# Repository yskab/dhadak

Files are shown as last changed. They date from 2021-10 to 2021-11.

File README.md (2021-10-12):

# धड़क\Dhadak - A Pulse Oximeter

<p align="middle">
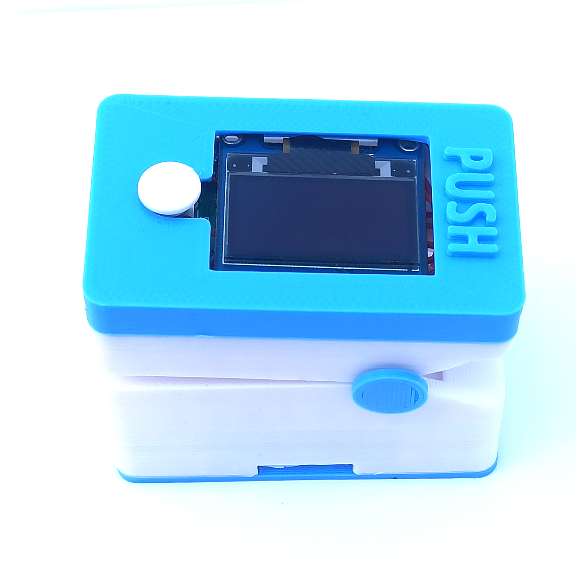
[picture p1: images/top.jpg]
  
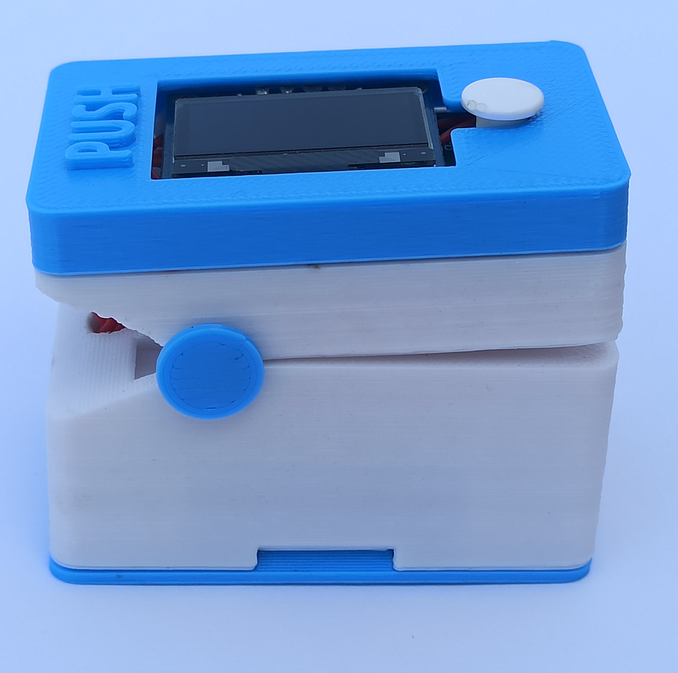
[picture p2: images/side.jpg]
   
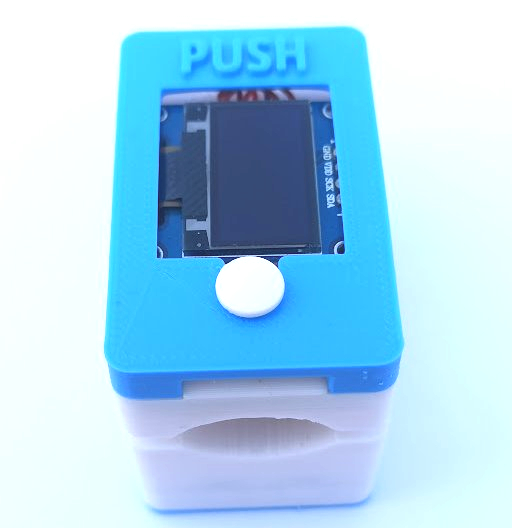
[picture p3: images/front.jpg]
  
</p>

* [Overview](#Overview)
* [Specifications](#Specifications)
* [Documentation](#Documentation)
* [Usage](#Usage)
* [Credits](#Credits)

## Overview

धड़क is a Pulse Oximeter which plugs onto a finger and measures
SpO<sub>2</sub>% and Heart rate of person.

<p align="center">
  spo2_gif
</p>

* Design doesn't use any specific oximeter sensor. A photodiode is used in the front end along with clean and amplify stages to obtain a suitable signal.

* ATmega4808 microcontroller is used in design along with QSB34CGR photodiode.

***Project Youtube video***

<div align="center">
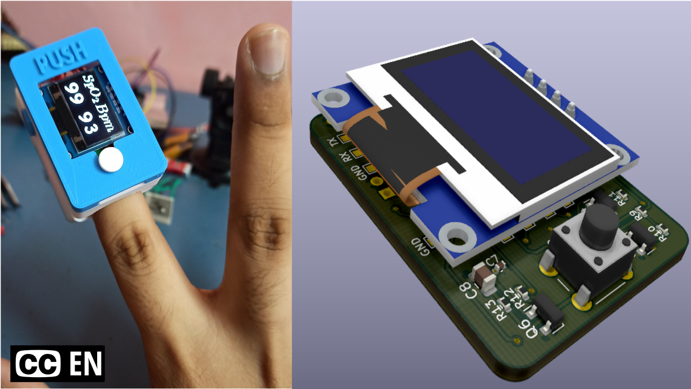
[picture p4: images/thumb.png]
Project Youtube video:
  
</div>

It was quite difficult to build a device that would work accurately for all finger types. Still, there are issues/improvements which I could think of in design, code & enclosure. Hence I decided to create an improvements section in each specific readme for the project directory. Anyone interested in building this project can refer to it and create a better device.

## Specifications
* Runs on 2 AAA Batteries (MN2400).
* Takes 15 secs max to find parameters (can find earlier, depends on subject's skin as leds adjust intensity to obtain a good response).
* Max average current draw: 25mA( This is the maximum draw when leds at full brightness). As per battery's datasheet and minimum operating voltage of 2.7V, this would give a continuous operation time of 13hrs. 
* 3 sec display update rate.
* Battery percentage indicator.
* Snap-fit enclosure with spring mechanism which ensures good firm contact of finger with photodiode.
* Soft latch power On/Off main button.
* 17KB Flash memory usage.

## Documentation

Complete understanding document detailing the overview, circuit design, block diagrams, and algorithm is available below for 2 languages:

[हिंदी दस्तावेज़](https://github.com/yskab/dhadak/blob/main/doc/hi/dhadak_hi.pdf)

[English doc](https://github.com/yskab/dhadak/blob/main/doc/en/dhadak_en.pdf)

## Usage
Repository Structure:

* **dhadak:** KiCAD Project files for v1.
* **dhadak_v2:** KiCAD Project files for v2.
* **doc:** Contains source for documentation.
* **enclosure:** FreeCAD project file.
* **firmware:** Source code.
* **images:** Device Images.
* **references:** PDF documents which were used as a reference to create the project.

Device was built as per KiCAD project: /dhadak. During testing, I later discovered that some things were simply not required to be added in design, so I desoldered certain circuit sections, amended the design, and wrote updated code/documentation around it. 

If you wish to build this device, please refer /dhadak_v2 project, it has the updated final schematics as per amendments in v1. Though PCB design was not done for this updated version, you can use the schematics present in the directory and build a PCB for it. Changes/amendments from v1 are mention in /dhadak_v2/readme.

### Programming Device

* For ATmega4808 first burn fuse to change clock to internal 8MHz.

* Proceed with code upload.

* Insert finger and press power button, wait for values to appear.

Please ensure to use good leds recommended for oximetry. I worked with generic ir & red leds which are used for indication applications hence SpO<sub>2</sub> was not quite accurate (as a healthy individual I should have got readings around 97+ but used to get around 90. This is the reason a small scaling factor has been added in code to compensate and calculate higher reading). These indication LEDs should not be used for oximeter. For best response, ensure LEDs have:

* Narrow view angle for less dispersion and deeper penetration into the skin.
* Rectangular package in the clear lens so that finger can rest comfortably.
* High radiant power.
	
A suitable choice can be Vishay Semiconductor's VSMD66694 or any other equivalent.

## Credits

**OLED Library:** ssd1306 by lexus2k

https://github.com/lexus2k/ssd1306

**OLED Images:** bmp2hex by Robert Gallup

https://github.com/robertgallup/python-bmp2hex

**Heart rate Algorithm:**

ArgÃijello-Prada, Erick Javier. The mountaineer’s method for
peak detection in photoplethysmographic signals. Revista Facul-
tad De Ingenieria-universidad De Antioquia 2018 (2019): 42-50

https://api.semanticscholar.org/CorpusID:116767900

**SpO<sub>2</sub> Algorithm:**

Michael W. Wukitsch, BA,Michael T. Petterson, BA, RRT, CPFT,
David R. Tobler, BSEE,and Jonas A. Pologe, BSEE
PULSE OXIMETRY: ANALYSIS OF THEORY, TECHNOLOGY, AND PRACTICE

https://link.springer.com/article/10.1007%2FBF01617328

All application notes/papers consulted in design can be found in the references directory.

## License
MIT License

Copyright (c) 2021 Y S K Abhijeet

Permission is hereby granted, free of charge, to any person obtaining a copy
of this software and associated documentation files (the "Software"), to deal
in the Software without restriction, including without limitation the rights
to use, copy, modify, merge, publish, distribute, sublicense, and/or sell
copies of the Software, and to permit persons to whom the Software is
furnished to do so, subject to the following conditions:

The above copyright notice and this permission notice shall be included in all
copies or substantial portions of the Software.

THE SOFTWARE IS PROVIDED "AS IS", WITHOUT WARRANTY OF ANY KIND, EXPRESS OR
IMPLIED, INCLUDING BUT NOT LIMITED TO THE WARRANTIES OF MERCHANTABILITY,
FITNESS FOR A PARTICULAR PURPOSE AND NONINFRINGEMENT. IN NO EVENT SHALL THE
AUTHORS OR COPYRIGHT HOLDERS BE LIABLE FOR ANY CLAIM, DAMAGES OR OTHER
LIABILITY, WHETHER IN AN ACTION OF CONTRACT, TORT OR OTHERWISE, ARISING FROM,
OUT OF OR IN CONNECTION WITH THE SOFTWARE OR THE USE OR OTHER DEALINGS IN THE
SOFTWARE.

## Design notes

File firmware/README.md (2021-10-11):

***src/main.cpp*** - source code

***src/bitmap.h*** - bitmap array of displayed images

***lib/ssd1306*** - ssd1306 library - https://github.com/lexus2k/ssd1306

Upload and device options configured in platformio.ini

Memory Usage:

RAM: 7.2% (used 441 bytes from 6144 bytes)

Flash: 35.3% (used 17327 bytes from 49152 bytes)

## Suggested Improvements

* Design can be comfortably completed on a 32KB flash device including any additional improvements. I had 10 units of ATmega4808, hence used it.

* Microseconds Delay in main loop sets the per-sample frequency (red and ir signal frequency) at around 500Hz. This is not a suitable approach, a better approach is to use timers, but I decided not to as it just worked fine.

* There is a slight step in the DAC Diff square wave signal before and after the sample signal. This is happening because DAC is called twice in a short interval( first to set diff level and then to set led brightness). This causes DACs diff output to add that slight step, though it's outside the signal, still a better approach is to improve the design and remove the step completely.

<p align="middle">
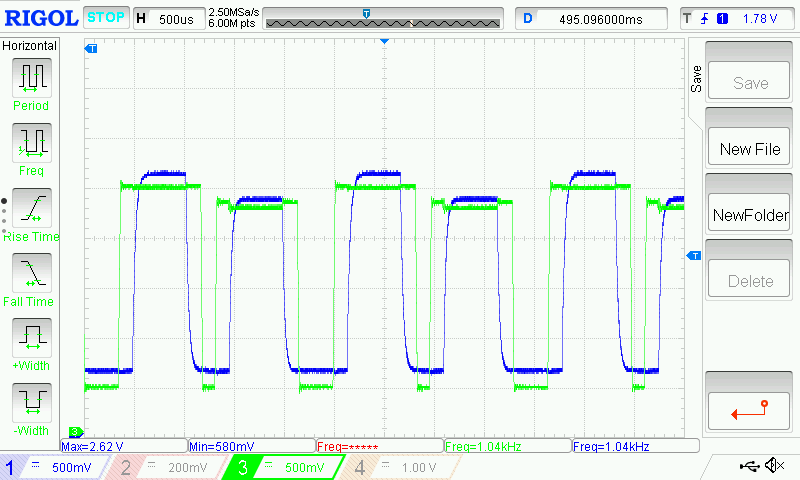
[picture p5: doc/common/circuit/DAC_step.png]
  
</p>

* Additional Algorithm can be implemented to take care of any motion-related errors.

* Generated diff signal can be made adaptable with I to V signal so that any slight variation in finger pressure or signal wobble, a new diff signal is immediately calculated and subtracted.

* Oled Updates values in real-time.

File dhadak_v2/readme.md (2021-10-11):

This KiCAD directory has the updated v2 schematics. PCB was not designed, PCB in v1 was amended to this schematic, so the actual code and documentation refer to this design. Changes in this schematics, when compared with v1, are:

* Increased Transimpedance Stage resistance to 576K. 200K was a bit lower, it is important to get a good response at this stage, hence the resistor was doubled.

* All resistors in difference amplifier changed to 10K. There is no need to have gain here. Fixed ADC ref at 1.1V and with oversampling, the response is quite good. Amplification can be added later in PGA.

* Removed isolation stage completely. No requirement to have separate isolation and Gain stages.

* A Single PGA stage is added, so any gain is applied equally to both red and ir.

* For a Quad opamp package, 1 opamp was left, so used it as a buffer.

* Removed R7 in series with infrared led. No need to limit ir current.

* 10u Bypass Cap on DAC didn't make any difference in ringing, removed it.

* Improved the Soft-latch circuit. Earlier Latch output was being used directly as Vcc. Since there are individual bypass capacitors also connected to DAC, ATmega, opamp, On to Off state was not working as the bypass capacitors were charged keeping the latch always turned On. In amended design, latch is completely local and Mosfet output drives Vcc, so latch can turn Off comfortably.

## Suggested Improvements
* A better PCB layout for I2C signals.
* Better bypassing of DAC, there was slight ringing at the edges, hence had to use a small delay before and after the waveform so that no spikes get included in difference amplifier output edges.

<p align="middle">
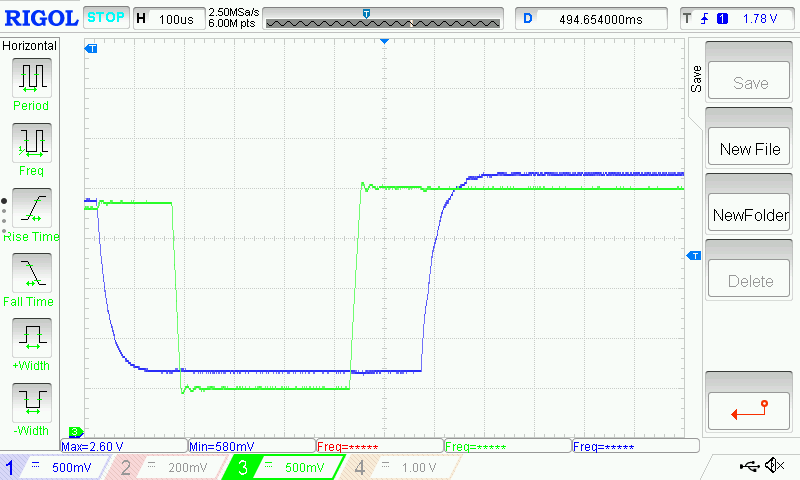
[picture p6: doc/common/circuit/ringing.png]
  
</p>

* Enclosure size was made as per battery lengths, PCB dimension could have been increased, allowing all the parts to fit in back, this would allow easy reflow of the backside and no hand soldering.

## Credits

* Latch circuit is taken from user Sam Raja's comment under EEVblog's Video: [EEVblog #262 - World's Simplest Soft Latching Power Switch Circuit](https://youtu.be/Foc9R0dC2iI)

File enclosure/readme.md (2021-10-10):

STLs folder has the actual STL files which i used for printing. I don't own a printer, so i sent the files to a external printing service who printed and shipped to me. Models were printed in PLA with 20% infill and with supports.

Minimum Finger Height: 9mm, if more than this, spring action takes place
Maximum Finger Width: 20mm	

## Suggested Improvements
* top part's snap fit is is a bit tight, it's hard to fit and remove, need to add some clearance.
*  Battery holding rectangle structures are asymmetrical, not equal dimensions.
* Some Spring inserts were tight but was able to fit at least one, which is good enough for test purposes and keeps pressure on the finger. A better design can be used for spring inserts instead of cylindrical holes. Also, actual springs can be used instead of re-purposing safety pins.

*   The pivot(circular tab part) was not able to fit in the spring  hinge as it was difficult to line up the spring with holes. Should have measure the lengths of springs before cutting them.

*   PCB fits nice, also when the top is closed, there is no wobble and things are tight.
*   It can be a bit difficult to put springs inside, doable with tweezers.
*   The battery wiring hole was a bad idea. It is difficult to get the wire through battery clips and supports had to be removed from that area which is difficult to do. Internal supports took a lot of time to remove so battery (+),(-) wiring needs a better approach.
*   upper wall in the led compartment should have been a little lower to allow the led to sit properly instead of slipping into the led wiring hole.
*   Led compartment should have been tighter to avoid glue.
*   I ordered wrong kind of battery clips. These were intended for series connections not for holding 2 AAAs. Had to snap one in half so that I can get (+) and (-).
*   Design to avoid internal support structures as they are difficult to remove.

## Credits for used external models

* Led: https://grabcad.com/library/3mm-led

* Switch 6x6: https://grabcad.com/library/tactile-switch-thru-6mm-series-1

* AAA Battery: https://grabcad.com/library/aaa-batterie-1

* Battery contact clip: https://www.keyelco.com/product.cfm/Slide-In-AAA-Battery-Contacts/5213/product_id/893

* Photodiode: https://octopart.com/qsb34cgr-on+semiconductor-84331133#CadModels

## Credits for Tutorials
As a complete beginner in FreeCAD, listed tutorials below helped me a lot to get to speed and start working on my model. I referred them throught the design. I would suggest anyone who is a beginner to start with these tutorials below for FreeCAD:

[Forum Discussion - Electronic Enclosure Arduino](https://youtu.be/6Nu8y0C0nvg)
Channel: [Learn FreeCAD](https://www.youtube.com/channel/UC_9HwDkwxllq5lFGkYBIH9g)

[FreeCad 0.18 Training Video inc. Kisslicer 3D Slicer](https://youtu.be/3w466yb255A)
Channel: [Ha Gei](https://www.youtube.com/channel/UCoe3BcVuLC9I2_yFud5vp8Q)

[FreeCAD Electronic Enclosure Using Simple Parametric Design Techniques](https://youtu.be/cJfbINgyz-k)
Channel: [Adventures in creation](https://www.youtube.com/channel/UC7pokUsRb6q2B0FOzSqQLlw)

Great tutorial by Adafruit for making snap fit cases
[# Layer by Layer – PyBadge Snapfit Case Pt 3](
https://youtu.be/pfBXfgCTmAU)

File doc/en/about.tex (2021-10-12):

During the COVID-19 wave in India, I saw a lot of people buying oximeters from medical stores and online to monitor oxygen levels at home. I was quite intrigued, how can a small device plugged to a finger could calculate heart rate and oxygen saturation? This question got me started to research and understand how these things actually work and whether I can make one from scratch. In the process I realized, it would be helpful to write all details in an understanding document which will serve as a memory to me and can be of help to others too.
Also, I wanted to start learning \LaTeX \hspace{1pt} so as to create beautiful written documents for all future projects.\medskip

This writing tries to present a brief theory of what oximetery is, how electronic components can be used to get the oxygen saturation value and heart rate. Required circuit block elements and algorithms have also been discussed. It has been assumed that reader has knowledge of:

\begin{itemize}
	\item Basic circuit analysis \& electronic components
	\item Opamp \& transistor working
\end{itemize}

\bigskip

I am a beginner in my electronics journey, hence there can be mistakes in this article. The accuracy of information presented has not been inspected by any other person than myself.
This guide was written so that it can become a source of knowledge to anyone trying to understand how to make an oximeter or how oximeter works. Presented design is not be used in any life support systems.

\bigskip
This document was written in TexStudio editor.

All pictures have been produced with Inkscape.

Plots were generated in GNU Octave.

PCB \& Schematics designed using Kicad.

Enclosure was designed in FreeCAD.

\medskip
All project related files are at: \url{https://github.com/yskab/dhadak}

Video series: \url{https://youtu.be/QoOAn5z_qHc}

For reporting any mistakes or corrections raise an issue on Github.

You can reach me on Twitter for posts and messages \href{https://twitter.com/yskabhijeet}{@yskabhijeet}

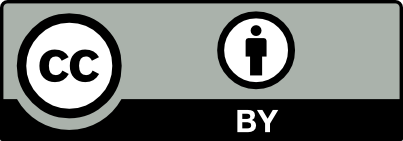
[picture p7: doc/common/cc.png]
\par

\vfill
\hfill
{\Large\bfseries Y S K Abhijeet}\par
\hfill
\large \today

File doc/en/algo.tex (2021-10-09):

\section{Algorithm}
	
	\begin{figure}[ht!]
		\hspace*{-1.8cm}
		\begin{tikzpicture}
			[node distance=1.5cm]
			
			\tikzstyle{startstop} = [rectangle, rounded corners, minimum width=3cm, minimum height=1cm,text centered, draw=black, fill=pink!30,align = center]
			
			\tikzstyle{io} = [trapezium, trapezium left angle=70, trapezium right 	angle=110, minimum width=3cm, minimum height=1cm, text centered, draw=black]
			
			\tikzstyle{process} = [rectangle, minimum width=3cm, minimum height=1cm, text 	centered, draw=black,align = center, fill = blue!20]
			
			\tikzstyle{decision} = [diamond, minimum width=3cm, minimum height=1cm, 
			align = center, draw=black, fill = green!20]
						
			\tikzstyle{arrow} = [thick,->,>=stealth]

			\node (st) [startstop] {Start};
			\node (pls) [process,below of=st] {Pulse leds};
			\node (wt) [process, below of=pls] {Wait 0.5 secs};
			\node (findlv) [decision, below of=wt,yshift=-1cm] {$V_1$ within\\preset levels};
			\node (setlv) [process, left of=findlv,xshift=-3cm] {Set new drive current};
			\node (dc) [process, below of=findlv,yshift=-1cm] {Find red/ir \\DC levels};
			\node (diff) [process, below of=dc] {Generate Diff signal};
			\node (amp) [decision, below of=diff,yshift=-1cm] {$V_2$ within\\ preset level};
			\node (pga) [process, left of=amp,xshift=-3cm] {PGA: Select gain\\ \& Amplify};
			\node (adc) [process, below of=amp,yshift=-1cm] {Read ADCs\\at every pulse};
			\node (filt) [process, below of=adc] {$2^{nd}$ order IIR filter};
			\node (peaks) [process, below of=filt] {Detect \\Peaks \& valley};
			\node (hr) [startstop,right of=peaks,xshift=+2.5cm] {Calculate HR};
			\node (ratio) [process,right of=filt,xshift=+2.5cm] {Calculate R Ratio};
			\node (spo2) [startstop,right of=ratio,xshift=+2.5cm] {Average \& \\Calculate $SpO_2$};
			
			\draw [arrow] (st) -- (pls);
			\draw [arrow] (pls) -- (wt);
			\draw [arrow] (wt) -- (findlv);
			\draw [arrow] (findlv) -- node [above]{False} (setlv);
			\draw [arrow] (setlv) |- (pls);
			\draw [arrow] (findlv) -- node [left]{True} (dc);
			\draw [arrow] (dc) -- (diff);
			\draw [arrow] (diff) -- (amp);
			\draw [arrow] (amp) -- node [above]{False} (pga);
			\draw [arrow] (amp) -- node [left]{True} (adc);
			\draw [arrow] (pga) |- (adc);
			\draw [arrow] (adc) -- (filt);
			\draw [arrow] (filt) -- (peaks);
			\draw [arrow](peaks) -- (hr);
			\draw [arrow](filt) -- (ratio);
			\draw [arrow](ratio) -- (spo2);		
		
			\draw (pls) ++(3.5,0) node [align = left]{\footnotesize
			red$\backslash$ir leds pulsed\\
			\footnotesize sequentially at $\SI{500}{\hertz}$};
			
			\draw (wt) ++(3.4,0) node [align = left]{\footnotesize
				wait 0.5 secs for\\\footnotesize PPG signal to settle};
			
			\draw (findlv) ++(3.7,0) node [align = left]{\footnotesize
				check if PPG signal\\\footnotesize within acceptable levels\\
				\footnotesize else inc/dec drive current};
			
			\draw (dc) ++(3.4,0) node [align = left]{\footnotesize
				determine red \& ir \\\footnotesize dc levels to generate\\
				\footnotesize diff signal};
			
			\draw (diff) ++(3.7,0) node [align = left]{\footnotesize
				DAC generates diff signal\\\footnotesize for DC subtraction};
			
			\draw (amp) ++(3.8,0) node [align = left]{\footnotesize
				Enable PGA if $V_2$\\\footnotesize not within acceptable level};
			
			\draw (ratio) ++(0,1) node [align = left]{\footnotesize
				R is found for\\\footnotesize consecutive samples};
			\draw (spo2) ++(0,1) node [align = left]{\footnotesize
				Average intermediate\\\footnotesize $SpO_2$ for final value};	
			
		\end{tikzpicture}
		\caption{Program Flow}
	\end{figure}
	
	\subsection{IIR Filter}

		ADC read samples can have little noise spikes which if passed directly to peak-valley detect function will lead to a lot of false detection and every peak-valley will not be captured accurately. A 2\textsuperscript{nd} order IIR filter is sufficient to smooth out the spikes before starting with estimations. Below is a 2\textsuperscript{nd} order IIR transfer function as difference equation:
		
		\[
		y_i = b_1*x_i + b_2*x_{i-2} - a_2*y_{i-1} + b_3*x_{i-1} - a_3*y_{i-2}
		\]
		
		where,
		
		$y_i$: current output
		
		$x_{i-1}$: previous input
		
		$y_{i-1}$: previous output
		
		$y_{i-2}$: output previous to $y_{i-1}$
		
		$x_i$: current input
		
		$x_{i-2}$: input previous to $x_{i-1}$

		\begin{figure}[ht!]
			\centering
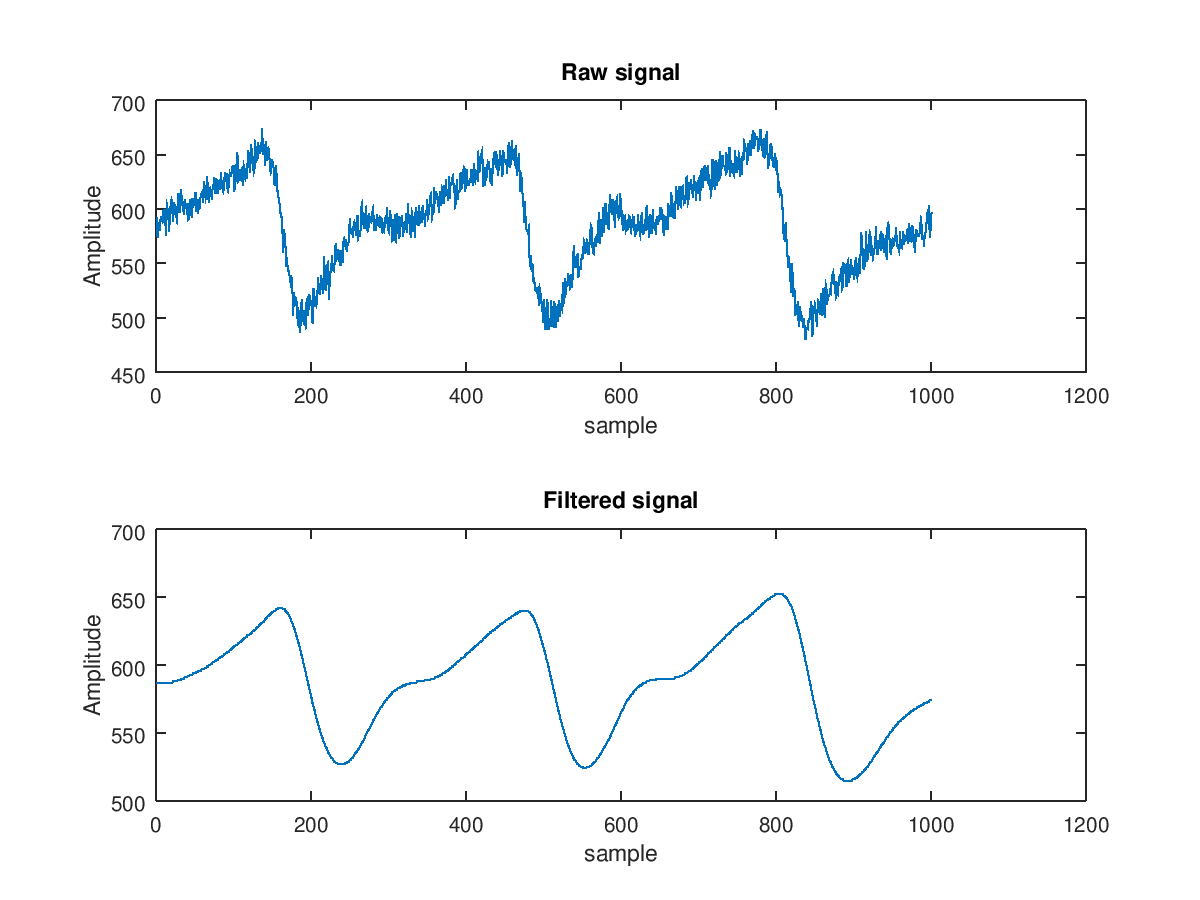
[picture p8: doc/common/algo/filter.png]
			
			\caption{2\textsuperscript{nd} order butterworth IIR filter}
			\label{fig:filter}
		\end{figure}
		
		Octave's $butter$ function\footnote{\url{https://octave.sourceforge.io/signal/function/butter.html}} was used to get the transfer function coefficients for a low pass configuration. Sampling frequency of 500Hz and a cut-off 3.3Hz (for max HR of 200) was used. Calculated below are the coefficient values:
		
		$a_2 = -1.94137, a_3 = 0.94304$
		
		$b_1 = b_3 = 4.1762e-04$
		
		$b_2 = 8.3523e-04$
		
		To visualize filter's performance, a raw signal was captured from ADC, filter equation was implemented and applied on the input signal in Octave. As seen in Figure \ref{fig:filter} filter is quite effective in suppressing noise and produces a smooth output\footnote{Only a 1\textsuperscript{st} order filter was implemented in actual program as it worked "just fine", but it is much better to have a 2\textsuperscript{nd} order filter for suitable filtering performance.}.

	\subsection{Heart Rate}
	
		HR is calculated using mountaineer's method for peak detection (MMPD) in photoplethysmographic signals\cite{mmpd}.
		
		In this method, slope is calculated for every sample and as slope changes from positive to negative, sample will corresponding to a peak. Similarly a slope change from negative to positive would be a valley. A count for positive or negative consecutive slopes is also taken and compared with a preset value which updates with every detected peak to improve the robustness of the algorithm. A timer running would store peak timings and time difference between consecutive peaks would correspond to the heart rate. Shown below is a visualization of the algorithm ran on a sample set. Peaks \& valleys are captured quite accurately.
		
		\begin{figure}[ht!]
			\centering
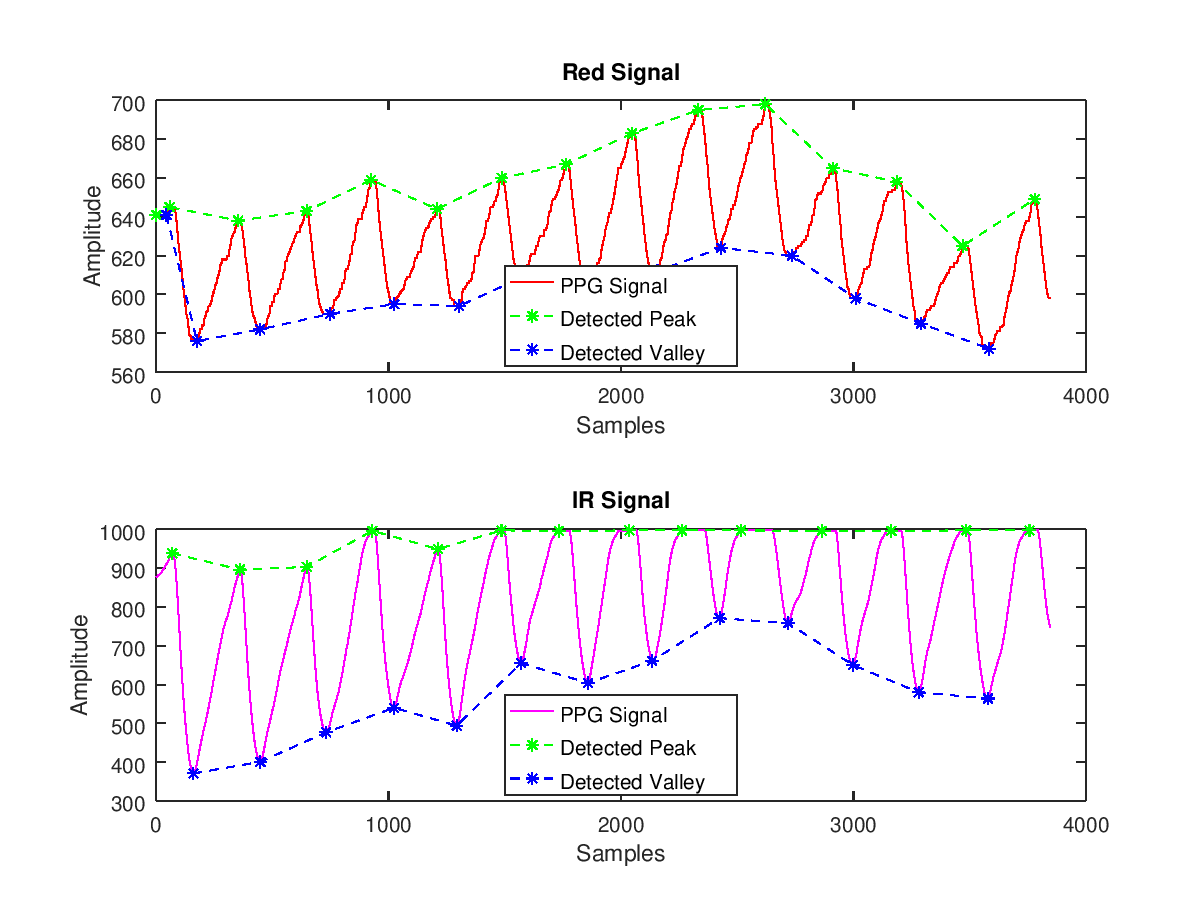
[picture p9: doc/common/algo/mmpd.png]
			
			\caption{HR Algorithm applied to sample data}
		\end{figure}
	
	\subsection{SpO\textsubscript{2} Calculation}
		
		As discussed previously in equation \eqref{eq:calc}:

		\[
			R = \sfrac{\frac{V_{p2} - V_{l2}}{DC_2}}{\frac{V_{p1} - V_{l1}}{DC_1}}
		\]	
		
		We don't want to use signal's actual peak and valleys for R calculation as that is dependent on heart rate and any averaging of values on top of that would delay the final SpO\textsubscript{2}\% which we intend to obtain. Hence a weight averaging method is used\cite{wuk}, where instantaneous SpO\textsubscript{2}\% is calculated for neighboring samples and averaged together. This ensure multiple instantaneous values are obtained which can be averaged to obtain a final value. Following steps are performed in order:
				
		\begin{figure}[ht!]
			\centering
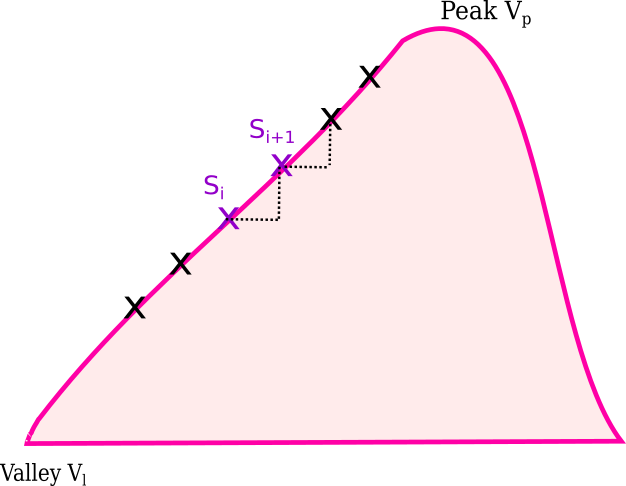
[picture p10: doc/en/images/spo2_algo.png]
			
			\caption{Selecting samples for instantaneous SpO\textsubscript{2}}
		\end{figure}
	
		\begin{enumerate}
			\item Find R between consecutive samples of red and ir signals: $S_{i+1}$ \& $S_{i}$. 
			
			\[
			R = \sfrac{\frac{S_{i_2+1} - S_{i2}}{DC_2}}{\frac{S_{i_1+1} - S_{i1}}{DC_1}}
			\]	
			
			Find SpO\textsubscript{2} with this R value which can obtained using a typical relationship curve equation as shown in Figure \ref{fig:curve}:
			\[		
				SpO_2 = -25*R + 110;
			\]
			\item Assign a weight to this SpO\textsubscript{2} based on the current average. If this instantaneous SpO\textsubscript{2} is lower than average, assign a lower weight. If nearer to average, assign a higher weight.
			
			\item Once weights are assigned for 20 samples, calculate a weighted average. Store this weighted average.
			
			\item Restart at step 1 and perform 10 such iterations.
			\item After 10 iterations, average the calculated weighted averages in each iteration. This becomes the final SpO\textsubscript{2}. Update this value with the current SpO\textsubscript{2} average which is used for assigning weights.
		\end{enumerate}
			
		A detailed explanation of this algorithm is in - Pulse Oximetry: Analysis of Theory, Technology and Practise\cite{wuk}
		
		Finally, an OLED display is refreshed every 5 secs with SpO\textsubscript{2}\% \& HR value.

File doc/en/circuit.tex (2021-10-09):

\section{Circuit Design}
	\begin{figure}[ht!]
	\begin{tikzpicture}
		[->,>=stealth',semithick]	
		\node[rectangle,draw] (r0) at (0, 0) {Photodiode};
		\node[rectangle,draw,text width=1cm, align=center] (r1) at (-1, -2) {RED LED};
		\node[rectangle,draw,text width=1cm, align=center] (r2) at (1, -2) {IR LED};	
		\node[rectangle,draw,text width=1cm, align=center] (r3) at (0, -4) {LED Driver};
		\node[rectangle,draw,text width=3cm, align=center] (r4) at (4, 0) {Transimpedance Amplifier};
		\node[rectangle,draw,text width=2cm, align=center] (r5) at (8, 0) {Difference  Amplifier};
		\node[rectangle,draw,text width=3cm, align=center] (r6) at (8, -2) {Programmable Gain Amplifier};
		\node[rectangle,draw,text width=1cm, align=center] (r7) at (8, -4) {$\mu$C ADC};
		\node[rectangle,draw,text width=1cm, align=center] (r8) at (2, -4) {$\mu$C};
		\node[rectangle,draw,text width=1cm, align=center] (r9) at (5, -2) {$\mu$C};
		
		\path (r1) edge (r0);
		\path (r2) edge (r0);
		\path (r3) edge (r1) 
		edge (r2);
		\path (r0) edge (r4);
		\path (r4) edge (r5);
		\path (r5) edge (r6);
		\path (r6) edge (r7);
		\path (r8) edge (r3);
		\path (r9) edge (r6);
		
	\end{tikzpicture}
	\caption{System Block Diagram}
	\end{figure}

	Referring the Block diagram, subsections are divided below that show the circuit and corresponding oscilloscope trace outputs.
	
	\subsection{Front End}	
	
		\subsubsection{Transimpedance Stage}
		
			Photodiode's current is needed to be converted to a proportional voltage so that ultimately the microcontoller can convert the voltage to a digital value using an ADC for calculation of SpO\textsubscript{2}. A simple Transimpedance Amplifier configuration was used to achieve this:
			
			\begin{figure}[ht!]\centering
				\begin{circuitikz}[american] 
					\draw
					
					(2,3) node[op amp,yscale=-1] (opamp) {}
					(opamp.down) -- +(0,0.3) node[vcc]{Vcc}
					(opamp.up) -- +(0,-0.3) node[ground]{}
					(0,0) node[ground]{} to[pDo, l^=$D$, f^=$I$]  (0,2.5) to (opamp.-)
					(opamp.+) node[ground]{}
					(opamp.-) -- ++(0,-1.7) -- ++(0.5,0)
					to [R, l^=$R_1$] ++(1.5,0) -- ++(0.4,0) to (opamp.out)
					(opamp.-)  ++(0,-1.7) -- ++(0,-1.3) -- ++(0.5,0) 
					to [C, l^=$C_1$]  ++(1.5,0) -- ++(0.4,0) -- ++(0,1.3) 
					(opamp.out) -- ++(1,0) to [open,v=$V_1$,o-o] ++(0,-3) node[ground]{};
					
				\end{circuitikz}
			\end{figure}

			As per led's intensity, if a current of 10$\mu$A is produced in the photodiode, and R = 100K$\Omega$, according to Ohm's law, $V_1$ = 1 V. Capacitor is used for low-pass filtering of the pulse. Cut off frequency would be:

			\begin{equation}	
				F_c = \frac{1}{2\pi R_1C_1}
			\end{equation}
		
			If R\textsubscript{1}=576K$\Omega$, C\textsubscript{1} = 33pF, 
			
			\[	
			F_c \approx \SI{8.3}{\kilo\hertz}
			\]
		
			\begin{figure}[ht!]
				\centering
				\subfloat[V\textsubscript{1} 
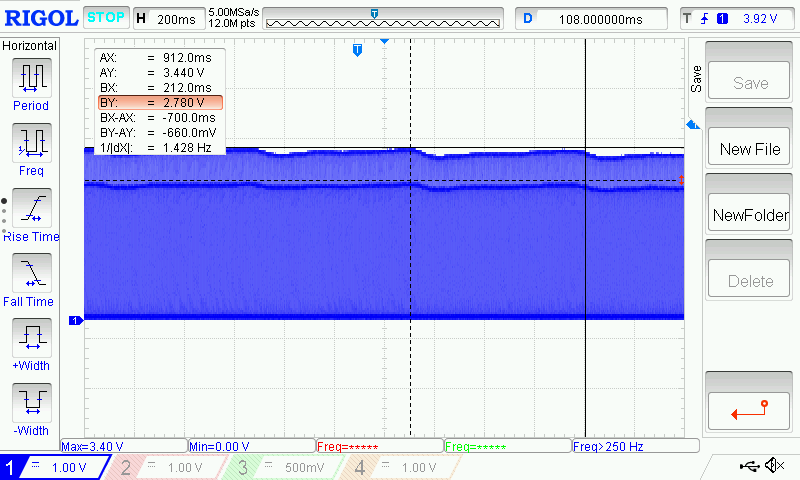
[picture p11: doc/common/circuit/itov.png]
				]{}
				\hfill
				\subfloat[V\textsubscript{1} zoomed in 
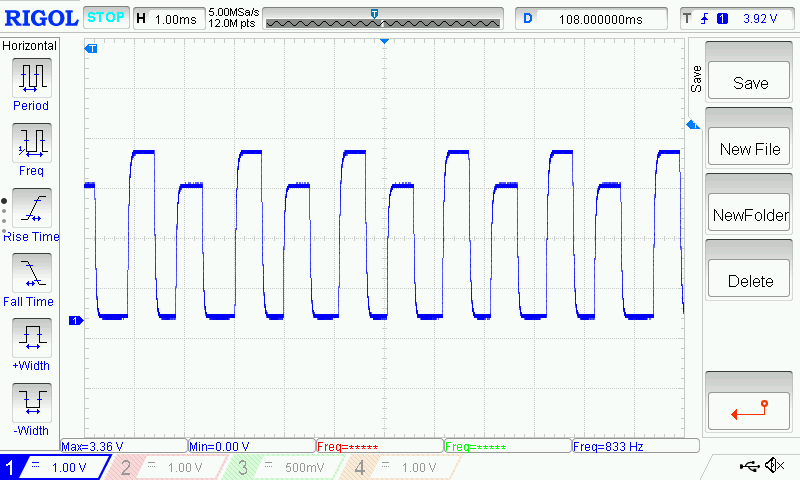
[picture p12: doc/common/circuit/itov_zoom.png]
				]{
				\label{fig:itov}}
				\caption{V\textsubscript{1} Oscilloscope trace (Red \& IR pulsed sequentially) }
			\end{figure}
		
			Since LEDs are pulse on-off at a fast rate sequentially the pulse would look like a square wave. We need to use a pulse frequency less than 1/10\textsuperscript{th} of this cut-off to pulse the LEDs so that the square wave with all its high-frequency components is clearly visible and not filtered out.
			
			\[	
			F_p = \SI{500}{\hertz}
			\]

			It can be seen in traces, 2 PPG signals are observable, riding on a DC level. Higher amplitude one is a result of ir led pulsing, while lower amplitude is from red led. Since the peaks correspond to heart rate, in this case as per trace, it measures out to be 1.42/sec or 85BPM. Individual pulses which construct the signal can be seen in Figure \ref{fig:itov}. Amplitude of detected red signal is lower than ir and that is due to:
			
			\begin{itemize}
				
				\item Higher intensity of ir led due to higher ir current.
				\item Photodiode's red sensitivity is 80\% of ir sensitivity. 
				\item Ir penetrates into skin deeper than red, hence a better ir response is visible at photodiode\cite{penetrate}.
				
			\end{itemize}		
			Hence to obtain a suitable response, it is important to increase led intensity until it reaches a required level so that the PPG signal has a higher amplitude.	
			
		\subsubsection{Difference Amplifier}
		
			PPG signal needs to be amplified to a suitable level so that full scale ADC range can be utilized to better digitize the signal. Right now, amplitude of PPG signal is quite low and DC level is higher. We are not bothered by the DC anymore, $\mu$C can read it and store for R value calculation, we only need to amplify the AC part which is an envelope of the signal. Direct amplification would lead to gain of the DC level as well, as the required signal is riding on top of it. This will saturate the opamp and amplification level range will be quite low. 
			
			\begin{figure}[ht!]
				\centering
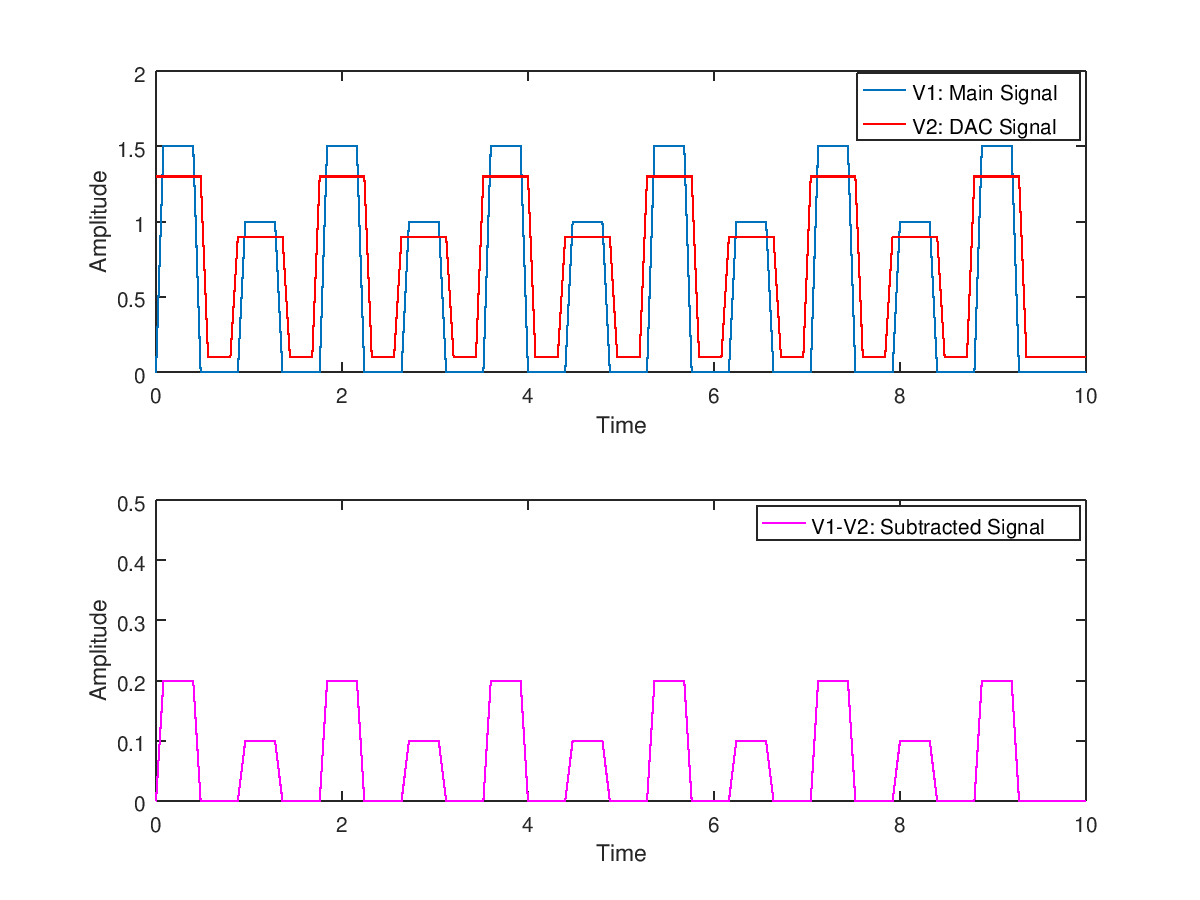
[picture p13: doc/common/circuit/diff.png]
				
				\caption{Effect of Difference Amplifier}
				\label{fig:diff}
			\end{figure}	
			
			If we can subtract the DC level from entire signal, only AC would remain which can be easily amplified further at higher levels. A Difference amplifier along with a 8bit Digital to analog converter (DAC) generating the DC cancellation signal can be used here. Since red and ir have different levels, separate DC levels are generated by DAC in sync with the pulsed frequency.\medskip 
			
			As shown in Figure \ref{fig:diff} a plot generated in Octave demonstrates subtraction of required signal and diff signal. This difference can then be amplified further. Pulse width of diff signal is slightly larger than required signal so that there are no spikes on edges in output signal. Also the lower level of diff signal is slightly above 0V to allow the difference to always be negative in low states and since negative supply is grounded, output would be 0V here.
			
			\begin{figure}[ht!]\centering
				\begin{circuitikz}[american] 
					\draw
					
					(4,3) node[op amp,yscale=-1] (opamp) {}
					(opamp.down) -- +(0,0.3) node[vcc]{Vcc}
					(opamp.up) -- +(0,-0.3) node[ground]{}
					(opamp.-) to [R, l^=$R_1$] ++(-2,0) node[label={left:$V_{dac1}$}] {}
					(opamp.+) to [R, l^=$R_1$] ++(-2,0) node[label={left:$V_1$}] {}
					(opamp.+) to [R, l^=$R_1$] ++(0,2) node[ground,rotate = 90]{}
					(opamp.-) -- ++(0,-1.7) -- ++(0.5,0)
					to [R, l^=$R_1$] ++(1.5,0) -- ++(0.4,0) to (opamp.out)
					(opamp.out) -- ++(1,0) to [open,v=$V_2$,o-o] ++(0,-3) node[ground]{};
			
				\end{circuitikz}
			\end{figure}

			\[
				V_2 = \frac{R_1}{R_1}(V_1 - V_{dac1})
			\]

			For $R_1 = 10K$,
			
			\[
				V_2 \approx V_1 - V_{dac1}
			\]

		\subsubsection{Programmable Gain Amplifier}
		
			It becomes necessary to amplify the signal as skin tone, improper finger contact with sensor or any skin pigmentation\cite{skin} can cause attenuation in signal leading to low amplitudes. This stage provides selectable variable gain which can be set by microcontroller.
			
			$\mu$C would determine what level of further amplification is required and drive the respective pin high so that resistor value would get selected.

			\begin{figure}[ht!]\centering
				\begin{circuitikz}[american] 
					\draw
						(2,3) node[op amp,yscale=-1] (opamp) {}
						(opamp.down) -- +(0,0.3) node[vcc]{Vcc}
						(opamp.up) -- +(0,-0.3) node[ground]{}
						(opamp.+) to ++(-2,0) node[label={left:$V_2$}] {}
						(opamp.-) -- ++(0,-1.7) -- ++(1,0)
						to [R, l^=$10K$] ++(1,0) -- ++(1,0) -- ++(0,2.2) to (opamp.out)
						(opamp.-) ++(0,-1.7) -- ++(0,-1.5) to [R, l^=$10K$] ++(0,-1) -- ++(0,-0.5)
						++(0,-0.5) node[npn] (Q1){}
						(Q1.E) node[ground]{}
						(Q1.B) to [R, l^=$4.7K$] ++(-1.5,0) node[label={left:S1}] {}
						
						(opamp.-) ++(0,-1.7) ++(0,-0.75) -- ++(3.5,0) -- ++(0,-0.75)		
						to [R, l^=$4.7K$] ++(0,-1) -- ++(0,-0.5)
						++(0,-0.5) node[npn] (Q2){}	
						(Q2.E) node[ground]{}	
						(Q2.B) to [R, l^=$4.7K$] ++(-1.5,0) node[label={left:S2}] {}
						
						(opamp.-) ++(0,-1.7) ++(0,-0.75) ++(2,0) -- ++(5,0) -- ++(0,-0.75)		
						to [R, l^=$2.35K$] ++(0,-1) -- ++(0,-0.5)
						++(0,-0.5) node[npn] (Q3){}	
						(Q3.E) node[ground]{}	
						(Q3.B) to [R, l^=$4.7K$] ++(-1.5,0) node[label={left:S3}] {};

				 \end{circuitikz}
			\end{figure}	
	
			\begin{center}
				\begin{tabular}{ |c|c|} 
					\hline
					\textbf{Switch} & \textbf{Gain}   \\ 
					\hline
					all off & 1 	\\ 
					\hline
					S1 & 2  		\\ 
					\hline
					S2 & 3  		\\ 
					\hline
					S1+S2 & 4  		\\ 
					\hline
					S3 & 5  		\\ 
					\hline
					S1+S3 & 6	  	\\ 
					\hline
					S2+S3 & 7  		\\ 
					\hline
				\end{tabular}
			\end{center}

	\subsection{LED Driver}

		As discussed previously, the detected signal levels can be very low after I to V stage. LED Driver needs to increase current to the leds as required. Following circuit is used as a voltage controlled current source, voltage is set by the DAC as instructed by the $\mu$C.
		
		\begin{figure}[ht!]\centering
			\begin{circuitikz}[american] 
				\draw
				
				(4,3) node[npn] (Q1){}
				(Q1.E) to [R, l^=20] ++(0,-1.5) node[ground]{}
				(Q1.B) to [R, l^=4.7K] ++(-1.5,0) node[label={left:$V_{dac2}$}] {}
				(Q1.C) -- ++(-1,0) -- ++(0,0.5) ++(0,0.5)  node[npn] (Q2){}
				(Q2.B) to [R, l_=10K] ++(-1.5,0) node[label={left:Red pulse}] {}
				(Q2.C) -- ++(0,1) node[]{} ++(0,0.2) node[]{Red cathode}
				(Q1.C) -- ++(1,0) -- ++(0,0.5) ++(0,0.5) node[npn,xscale=-1] (Q3){}
				(Q3.B) to [R, l^=10K] ++(1.5,0) node[label={right:IR pulse}] {}
				(Q3.C) to ++(0,1) node[]{} ++(0,0.2) node[]{Ir cathode};
			\end{circuitikz}
		\end{figure}

		Leds get activated by a single bridge configuration, whenever red/ir pulse is active, corresponding red/ir leds get active (led anodes connected to Vcc). Amount of current would depend on $V_{dac2}$ \& $R_1$.
		
		$V_{dac2}$ is also set individually for red and ir as per the pulsed frequency. If intensity is not sufficient for signal detection, it is necessary to increase $V_{dac2}$. $\mu$C would determine the thresholds and modulate the control voltage accordingly.
	
		Shown below is final output after the PGA stage.
		The gained up PPG signal is clearly visible for both red and ir which is at a suitable level for ADC capture and usage in algorithms for calculations.

	\begin{figure}[ht!]
		\centering
		\subfloat[Final output - green, V\textsubscript{1} - blue
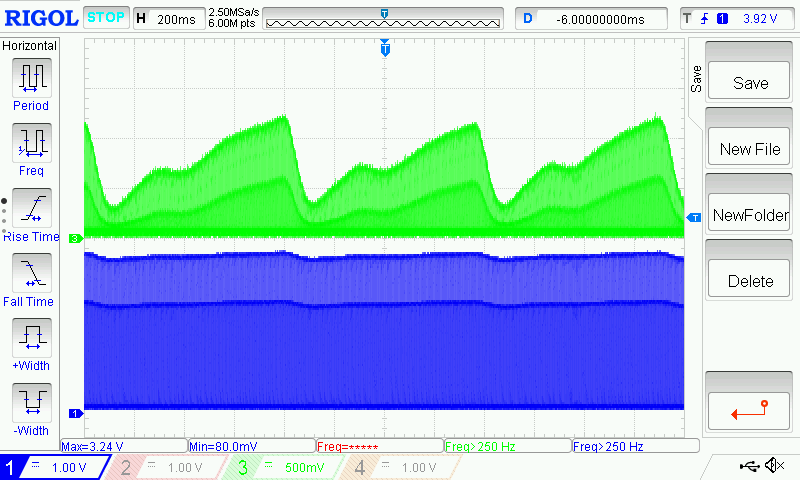
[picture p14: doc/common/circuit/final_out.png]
		]{}
		\hfill
		\subfloat[Final output measurement
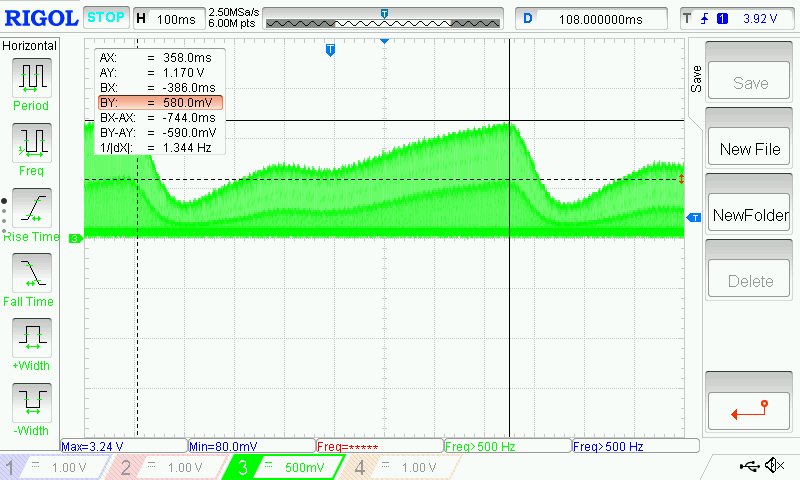
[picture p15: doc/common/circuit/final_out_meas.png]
		]{}
		\caption{Final output}
	\end{figure}

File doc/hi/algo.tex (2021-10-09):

\section{ऐल्गोरिद्म}
	
	\begin{figure}[ht!]
		\hspace*{-1.8cm}
		\begin{tikzpicture}
			[node distance=1.5cm]
			
			\tikzstyle{startstop} = [rectangle, rounded corners, minimum width=3cm, minimum height=1cm,text centered, draw=black, fill=pink!30,align = center]
			
			\tikzstyle{io} = [trapezium, trapezium left angle=70, trapezium right 	angle=110, minimum width=3cm, minimum height=1cm, text centered, draw=black]
			
			\tikzstyle{process} = [rectangle, minimum width=3cm, minimum height=1cm, text 	centered, draw=black,align = center, fill = blue!20]
			
			\tikzstyle{decision} = [diamond, minimum width=3cm, minimum height=1cm, 
			align = center, draw=black, fill = green!20]
						
			\tikzstyle{arrow} = [thick,->,>=stealth]

			\node (st) [startstop] {शुरु};
			\node (pls) [process,below of=st] {led पल्स शुरू};
			\node (wt) [process, below of=pls] {0.5 सेकंड प्रतीक्षा};
			\node (findlv) [decision, below of=wt,yshift=-1cm] {$V_1$ निर्धारित स्तर\\के अन्तर्गत};
			\node (setlv) [process, left of=findlv,xshift=-3cm] {नया ड्राइव करंट सेट करें};
			\node (dc) [process, below of=findlv,yshift=-1cm] {लाल/इन्फ़रा का \\DC स्तर खोजें};
			\node (diff) [process, below of=dc] {डिफ सिग्नल उत्पन्न करें};
			\node (amp) [decision, below of=diff,yshift=-1cm] {$V_2$ निर्धारित \\ स्तर के अन्तर्गत};
			\node (pga) [process, left of=amp,xshift=-3cm] {PGA: बढ़त चुन\\कर एम्प्लिफ़्य};
			\node (adc) [process, below of=amp,yshift=-1cm] {प्रत्येक पल्स पर\\ADC पढ़ें};
			\node (filt) [process, below of=adc] {$2^{nd}$ ऑर्डर IIR फ़िलटर};
			\node (peaks) [process, below of=filt] {शिखर - घाटी का \\पता लगाएं};
			\node (hr) [startstop,right of=peaks,xshift=+2.5cm] {HR की गणना};
			\node (ratio) [process,right of=filt,xshift=+2.5cm] {R अनुपात की गणना};
			\node (spo2) [startstop,right of=ratio,xshift=+2.5cm] {औसत $SpO_2$\& \\कि गणना};
			
			\draw [arrow] (st) -- (pls);
			\draw [arrow] (pls) -- (wt);
			\draw [arrow] (wt) -- (findlv);
			\draw [arrow] (findlv) -- node [above]{गलत} (setlv);
			\draw [arrow] (setlv) |- (pls);
			\draw [arrow] (findlv) -- node [left]{सही} (dc);
			\draw [arrow] (dc) -- (diff);
			\draw [arrow] (diff) -- (amp);
			\draw [arrow] (amp) -- node [above]{गलत} (pga);
			\draw [arrow] (amp) -- node [left]{सही} (adc);
			\draw [arrow] (pga) |- (adc);
			\draw [arrow] (adc) -- (filt);
			\draw [arrow] (filt) -- (peaks);
			\draw [arrow](peaks) -- (hr);
			\draw [arrow](filt) -- (ratio);
			\draw [arrow](ratio) -- (spo2);	

			\draw (pls) ++(3.6,0) node [align = left]{\footnotesize
			लाल$\backslash$इन्फ़्रारेड led क्रमिक\\
			\footnotesize रूप से चालु $\SI{500}{\hertz}$ पे};
			
			\draw (wt) ++(3.5,0) node [align = left]{\footnotesize
			0.5 सेकंड प्रतीक्षा PPG\\\footnotesize सिग्नल ठहराने के लिए};
			
			\draw (findlv) ++(3.7,0) node [align = left]{\footnotesize
			जाँचे PPG सिग्नल निर्धारित \\\footnotesize स्तर के अन्तर्गत नहीं तो\\
			\footnotesize नया ड्राइव करंट सेट करें};
			
			\draw (dc) ++(3.4,0) node [align = left]{\footnotesize
			लाल/इन्फ़रा DC स्तर \\\footnotesize खोजें डिफ़ सिगनल \\\footnotesize के लिये};

			\draw (diff) ++(3.6,0) node [align = left]{\footnotesize
			DAC डिफ़ सिगनल उत्पन्न \\\footnotesize करेगा DC घटाव के लिये};
			
			\draw (amp) ++(3.4,0) node [align = left]{\footnotesize
			PGA सक्षम करें यदि\\\footnotesize $V_2$ स्वीकार्य स्तर के \\\footnotesize भीतर नही हो};
			
			\draw (ratio) ++(0,1) node [align = left]{\footnotesize
				R कि गणाना\\\footnotesize पडोसी समंक बिन्दुओ से};
			\draw (spo2) ++(0,1) node [align = left]{\footnotesize
				मध्यवर्ती $SpO_2$ का\\\footnotesize औसत अंतिम मूल्य के लिए};
			
		\end{tikzpicture}
		\caption{योजना प्रवाह}
	\end{figure}
	
	\subsection{IIR फ़िलटर}

		ADC से पड़े सिगनल मे शोर हो सकता है, यदि यह सिगनल सीधे शिखर - घाटी की खोज मे प्रयोग कर दिया गया, तो बहुत सारी शिखर - घाटी सटीक रूप से नहीं मिलेगा शोर के कारण। इसलिये यह ज़रुरी है कि शोर को न्यूनतम करा जा सके। 
		एक 2\textsuperscript{nd} ऑर्डर IIR फ़िलटर सिगनल को सुचारु करने के लिए पर्याप्त है। अंतर समीकरण के रूप में 2\textsuperscript{nd} ऑर्डर IIR ट्रांसफर फ़ंक्शन नीचे दिया गया है:
		
		\[
		y_i = b_1*x_i + b_2*x_{i-2} - a_2*y_{i-1} + b_3*x_{i-1} - a_3*y_{i-2}
		\]
		
		जाहा,
		
		$y_i$: मौजूदा आउटपुट
		
		$y_{i-1}$: पिछला आउटपुट
		
		$y_{i-2}$: $y_{i-1}$ का पिछला आउटपुट
		
		$x_i$: मौजूदा इनपुट
		
		$x_{i-1}$: पिछला इनपुट
		
		$x_{i-2}$: $x_{i-1}$ का पिछला इनपुट
		
		\begin{figure}[ht!]
			\centering
			
			\caption{2\textsuperscript{nd} ऑर्डर बटरवर्थ IIR फ़िलटर}
			\label{fig:filter}
		\end{figure}
		
		Octave's $butter$ function\footnote{\url{https://octave.sourceforge.io/signal/function/butter.html}} का प्रयोग लो पास कॉन्फ़िगरेशन के लिए स्थानांतरण फ़ंक्शन गुणांक प्राप्त करने के लिए किया गया था।  Sampling आवृत्ति 500Hz और cut-off 3.3Hz (अधिकतम HR 200 के लिये) दिया गया था। गुणांक मान:
		
		$a_2 = -1.94137, a_3 = 0.94304$
		
		$b_1 = b_3 = 4.1762e-04$
		
		$b_2 = 8.3523e-04$	
		
		फ़िल्टर के प्रदर्शन को स्पष्ट करने के लिए, ADC से लाल सिग्नल लिया गया था, फ़िल्टर समीकरण लागू किया गया था Octave मे। जैसा कि चित्र \ref{fig:filter} में देखा गया है, फ़िल्टर शोर को दबाने में काफ़ी प्रभावी है और एक सहज आउटपुट\footnote{वास्तविक प्रोग्राम में केवल 1\textsuperscript{st} ऑर्डर फ़िल्टर लागू किया गया था क्योंकि वह अच्छा काम कर रहा था, लेकिन उपयुक्त फ़िल्टरिंग प्रदर्शन के लिए 2\textsuperscript{nd} ऑर्डर फ़िल्टर होना बहुत बेहतर है।} उत्पन्न करता है।

	\subsection{हृदय गति}
	
		हृदय गति गणना mountaineer's method for peak detection (MMPD)\cite{mmpd} ऐल्गोरिद्म से करी गयी है। 
		
		इस पद्धति में, प्रत्येक बिन्दु के लिए ढलान की गणना की जाती है और जैसे-जैसे ढलान सकारात्मक से ऋणात्मक में बदलता है, बिन्दु एक शिखर के अनुरूप होगा। इसी तरह एक ढलान का ऋणात्मक से सकारात्मक में परिवर्तन एक घाटी होगा। सकारात्मक या ऋणात्मक लगातार ढलानों के लिए एक गिनती भी ली जाती है और एक पूर्व निर्धारित मूल्य के साथ तुलना की जाती है जो ऐल्गोरिद्म की सुधार करने के लिए प्रत्येक ज्ञात शिखर के साथ अद्यतन होता है।
		
		एक टाइमर शिखर टाइमिंग को स्टोर करेगा और लगातार चोटियों के बीच समय का अंतर हृदय गति (HR) के अनुरूप होगा।
		
		\begin{figure}[ht!]
			\centering
			
			\caption{डेटा पर लागू ऐल्गोरिद्म}
		\end{figure}
	
	\subsection{SpO\textsubscript{2} गणना}
		
		जेसा कि पहले समीकरण \eqref{eq:calc} मे देखा गया हे:
		
		\[
			R = \sfrac{\frac{V_{p2} - V_{l2}}{DC_2}}{\frac{V_{p1} - V_{l1}}{DC_1}}
		\]	
		
		हम R कि गणना के लिए सिग्नल के वास्तविक शिखर और घाटियों का उपयोग नहीं करना चाहते हैं क्योंकि यह हृदय गति पर निर्भर है और यदि औसत निकाला जाये इस गणना से विभिन्न बिंदुओं के लिए तो अंतिम SpO\textsubscript{2}\% प्रपात करने में देरी होगी। इसलिए एक वज़न औसत विधि\cite{wuk} का उपयोग किया जाता है, जहां तात्कालिक SpO\textsubscript{2}\% की गणना पड़ोसी बिंदुओं के लिए की जाती है और एक साथ औसत करी जाती है। यह सुनिश्चित करता है कि कई तात्कालिक मूल्य प्राप्त होते हैं जिन्हें अंतिम मूल्य प्राप्त करने के लिए औसत किया जा सकता है। इस विधि मे निम्नलिखित चरणों को क्रम में किया जाता है:
		
		\begin{figure}[ht!]
			\centering
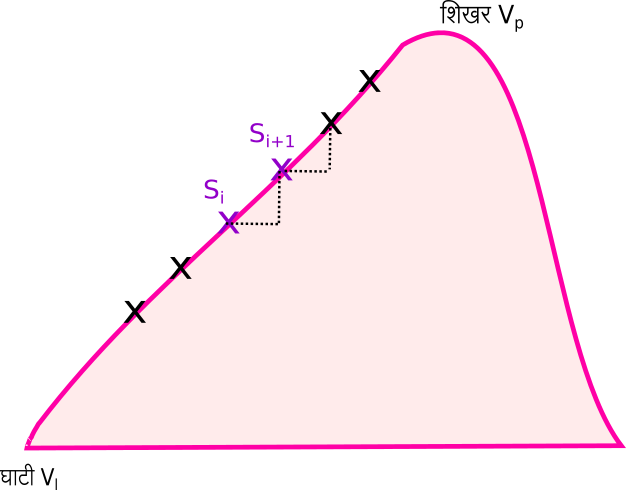
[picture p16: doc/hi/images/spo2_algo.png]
			
			\caption{तात्कालिक SpO\textsubscript{2} के लिये चयनित बिन्दु}
		\end{figure}
	
		\begin{enumerate}
			\item लाल और इन्फ़्रारेड बिन्दुओ के क्रमागत नमूनों के बीच R प्रापत करना होगा: $S_{i+1}$ \& $S_{i}$. 
			
			\[
				R = \sfrac{\frac{S_{i_2+1} - S_{i2}}{DC_2}}{\frac{S_{i_1+1} - 		S_{i1}}{DC_1}}
			\]	
			
			इस R मान के साथ SpO\textsubscript{2} खोजें, जो एक विशिष्ट संबंध वक्र समीकरण का उपयोग करके प्राप्त किया जा सकता है जेसा कि चित्र \ref{fig:curve} मे देखा गया था:
			\[		
			SpO_2 = -25*R + 110;
			\]
			
			\item वर्तमान औसत के आधार पर इस SpO\textsubscript{2} को भार दें। यदि यह तात्कालिक SpO\textsubscript{2} औसत से कम है, तो कम भार निर्दिष्ट करें। यदि औसत के करीब है, तो अधिक भार निर्दिष्ट करें। 
			
			\item 20 बिन्दुओ के लिए भार सौंपे जाने के बाद, एक भारित औसत की गणना करें। इस भारित औसत को स्टोर करें।
			
			\item चरण 1 पर पुनरारंभ करें और ऐसे 10 पुनरावृत्तियों को निष्पादित करें।
			
			\item 10 पुनरावृत्तियों के बाद, प्रत्येक पुनरावृत्ति में परिकलित भारित औसत का औसत करे। यह अंतिम SpO\textsubscript{2} बन जाता है। इस मान को वर्तमान SpO\textsubscript{2} औसत से अपडेट करें जिसका उपयोग भार निर्दिष्ट करने के लिए किया जाता है।

		\end{enumerate}
	
		इस एल्गोरिथम का विस्तृत विवरण में मौजूद है - Pulse Oximetry: Analysis of Theory, Technology and Practise\cite{wuk}		

		अंत में, प्रत्येक 5 सेकंड में एक OLED डिस्प्ले पर SpO\textsubscript{2}\% और HR का मान प्रदर्शित किया जाता है।

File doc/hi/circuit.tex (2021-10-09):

\section{सर्किट डिज़ाइन}
	\begin{figure}[ht!]
	\begin{tikzpicture}
		[->,>=stealth',semithick]	
		\node[rectangle,draw] (r0) at (0, 0) {फोटोडायोड};
		\node[rectangle,draw,text width=1cm, align=center] (r1) at (-1, -2) {लाल LED};
		\node[rectangle,draw,text width=1cm, align=center] (r2) at (1, -2) {इन्फ़्रारेड LED};	
		\node[rectangle,draw,text width=1cm, align=center] (r3) at (0, -4) {LED चालक};
		\node[rectangle,draw,text width=3cm, align=center] (r4) at (4, 0) {ट्रांस्इम्पेडेंस एम्पलीफायर};
		\node[rectangle,draw,text width=2cm, align=center]  (r5) at (8, 0) {डिफ़ैंस एम्पलीफायर};
		\node[rectangle,draw,text width=2cm, align=center] (r6) at (8, -2) {प्रोग्रामेबल गेन एम्प्लिफायर};
		\node[rectangle,draw,text width=3cm, align=center] (r7) at (8, -4) {$\mu$C ADC};
		\node[rectangle,draw,text width=1cm, align=center] (r8) at (2, -4) {$\mu$C};
		\node[rectangle,draw,text width=1cm, align=center] (r9) at (5, -2) {$\mu$C};
		
		\path (r1) edge (r0);
		\path (r2) edge (r0);
		\path (r3) edge (r1) 
		edge (r2);
		\path (r0) edge (r4);
		\path (r4) edge (r5);
		\path (r5) edge (r6);
		\path (r6) edge (r7);
		\path (r8) edge (r3);
		\path (r9) edge (r6);
		
	\end{tikzpicture}
	\caption{सिस्टम ब्लॉक आकृति}
	\end{figure}

	ब्लॉक आकृति का जिक्र करते हुए, उपखंड नीचे विभाजित हैं जो सर्किट और संबंधित आसिलोस्कोप ट्रेस आउटपुट दिखाते हैं।
	
	\subsection{फ्रंट एंड}	
	
		\subsubsection{ट्रांस्इम्पेडेंस भाग}
		
			फोटोडायोड के करंट को आनुपातिक वोल्टेज में बदलने की आवश्यकता होती है ताकि अंततः माइक्रोकंट्रोलर SpO\textsubscript{2} की गणना के लिए ADC का उपयोग करके वोल्टेज को डिजिटल मान में परिवर्तित कर सके। इसे प्राप्त करने के लिए एक साधारण ट्रांजिम्पेडेंस एम्प्लीफायर कॉन्फ़िगरेशन का उपयोग किया गया हैं:

			\begin{figure}[ht!]\centering
				\begin{circuitikz}[american] 
					\draw
					
					(2,3) node[op amp,yscale=-1] (opamp) {}
					(opamp.down) -- +(0,0.3) node[vcc]{Vcc}
					(opamp.up) -- +(0,-0.3) node[ground]{}
					(0,0) node[ground]{} to[pDo, l^=$D$, f^=$I$]  (0,2.5) to (opamp.-)
					(opamp.+) node[ground]{}
					(opamp.-) -- ++(0,-1.7) -- ++(0.5,0)
					to [R, l^=$R_1$] ++(1.5,0) -- ++(0.4,0) to (opamp.out)
					(opamp.-)  ++(0,-1.7) -- ++(0,-1.3) -- ++(0.5,0) 
					to [C, l^=$C_1$]  ++(1.5,0) -- ++(0.4,0) -- ++(0,1.3) 
					(opamp.out) -- ++(1,0) to [open,v=$V_1$,o-o] ++(0,-3) node[ground]{};
					
				\end{circuitikz}
			\end{figure}

			Led की तीव्रता के अनुसार, यदि फोटोडायोड में 10$\mu$A का करंट उत्पन्न होता है, और R = 100K$\Omega$, ओम के नियम के अनुसार, $V_1$ = 1 V। 
			कैपेसिटर का उपयोग पल्स कि लो-पास फ़िल्टरिंग के लिए किया जाता है। कट ऑफ आवृत्ति होगी:
		
			\begin{equation}	
				F_c = \frac{1}{2\pi R_1C_1}
			\end{equation}
			
			यदि R\textsubscript{1}=576K$\Omega$, C\textsubscript{1} = 33pF, 

			\[	
			F_c \approx \SI{8.3}{\kilo\hertz}
			\]
			
			\begin{figure}[ht!]
				\centering
				\subfloat[V\textsubscript{1} 
				]{}
				\hfill
				\subfloat[V\textsubscript{1} ज़ूम 
				]{
				\label{fig:itov}}
				\caption{V\textsubscript{1} ऑसिलोस्कोप ट्रेस (लाल \& इन्फ़्रारेड क्रमिक रूप से स्पंदित) }
			\end{figure}
			
			चूंकि led क्रमिक रूप से तेज दर के साथ ऑन-ऑफ होते हैं, इसलिए पल्स एक वर्ग तरंग की तरह दिखाई देगा। हमें led को स्पंदित करने के लिए इस कट-ऑफ के 1/10\textsuperscript{th} से कम पल्स फ्रीक्वेंसी का उपयोग करने होगा ताकि इसके सभी उच्च-आवृत्ति घटकों के साथ वर्ग तरंग स्पष्ट रूप से दिखाई दे और फ़िल्टर न हो।
			
			\[	
			F_p = \SI{500}{\hertz}
			\]

			यह ट्रेस में देखा जा सकता है, डीसी स्तर के उपर 2 PPG सिग्नल मोजुद हैं।
			उच्च आयाम इन्फ़्ररेड स्पंदन का परिणाम है, जबकि निचला आयाम लाल का है। चूँकि चोटियाँ हृदय गति के अनुरूप होती हैं, ट्रेस अनुसार यह 1.42/सेकंड या 85BPM है। सिग्नल का निर्माण करने वाली व्यक्तिगत स्पंद को चित्र \ref{fig:itov} में देखा जा सकता है। ज्ञात रेड सिग्नल का आयाम इन्फ़्ररेड से कम है, इसके कारण है:
			
			\begin{itemize}
				
				\item इन्फ्रारेड कि जादा तीव्रता उच्च इन्फ़्रारेड करंट के कारण।
				\item फोटोडायोड की लाल संवेदनशीलता इन्फ्रारेड संवेदनशीलता का 80\% है। 
				\item इन्फ्रारेड त्वचा में लाल से अधिक गहराई तक प्रवेश करता है, इसलिए फोटोडायोड पर बेहतर इन्फ्रारेड प्रतिक्रिया दिखाई देती है\cite{penetrate}। 
				
			\end{itemize}		
		
			इसलिए एक उपयुक्त सिगनल प्राप्त करने के लिए आवश्यक हे led की तीव्रता को बढ़ाना ताकि PPG सिग्नल का आयाम उच्च हो सके।	
			
		\subsubsection{डिफ़ैंस एम्पलीफायर}
		
			PPG सिग्नल को उपयुक्त स्तर तक बढ़ाने की जरूरत है ताकि सिग्नल को बेहतर ढंग से डिजिटाइज करने के लिए पूर्ण पैमाने पर ADC रेंज का उपयोग किया जा सके। अभी, PPG सिग्नल का आयाम काफी कम है और डीसी स्तर अधिक है। $\mu$C  DC को पढ़ सकता हैं और आर मूल्य गणना के लिए स्टोर कर सकता हैं, हमें केवल AC भाग को बढ़ाना होगा जो सिग्नल का एक आवरण है। प्रत्यक्ष बढ़ोतरी से डीसी स्तर भी प्राप्त होगा, क्योंकि आवश्यक संकेत इसके ऊपर सवार है। यह ऑप एंप को संतृप्त करेगा और बढ़ोतरी स्तर की सीमा काफी कम होगी।

			\begin{figure}[ht!]
				\centering
				
				\caption{डिफ़ैंस एम्पलीफायर का प्रभाव}
				\label{fig:diff}
			\end{figure}	
			
			यदि हम DC स्तर को पूरे सिग्नल से घटा सकें, तो केवल AC ही रहेगा जिसके स्तर को आसानी से आगे बढ़ाया जा सक़ता है। यह DC संकेत उत्पन्न करने के लिए 8 बिट डिजिटल से एनालॉग कनवर्टर (DAC) के साथ एक डिफ़ैंस एम्प्लीफायर का उपयोग यहां किया गया है। चूंकि लाल और इन्फ़्ररेड के अलग-अलग स्तर होते हैं, इसलिए DAC द्वारा स्पंदित आवृत्ति के अनुसार अलग-अलग डीसी स्तर उत्पन्न होते हैं।
			\medskip 
			
			जैसा कि चित्र \ref{fig:diff} में दिखाया गया है, Octave में उत्पन्न एक प्लॉट आवश्यक सिग्नल और डिफ़ैंस सिग्नल के घटाव को दर्शाता है। अब इस अंतर को और आगे बढ़ाया जा सक़ता है। डिफ़ैंस सिग्नल की पल्स चौड़ाई आवश्यक सिग्नल से थोड़ी बड़ी होती है ताकि आउटपुट सिग्नल में किनारों पर कोई स्पाइक न हो। डिफ़ैंस सिग्नल का निचला स्तर 0V से थोड़ा ऊपर है, जिससे अंतर हमेशा आवश्यक सिग्नल के 0V क्षेत्र में नकारात्मक हो और चूंकि ओप-अम्प एकल आपूर्ति पर परिचालन कर रहा है, इसलिए आउटपुट यहां 0V होगा।

			\begin{figure}[ht!]\centering
				\begin{circuitikz}[american] 
					\draw
					
					(4,3) node[op amp,yscale=-1] (opamp) {}
					(opamp.down) -- +(0,0.3) node[vcc]{Vcc}
					(opamp.up) -- +(0,-0.3) node[ground]{}
					(opamp.-) to [R, l^=$R_1$] ++(-2,0) node[label={left:$V_{dac1}$}] {}
					(opamp.+) to [R, l^=$R_1$] ++(-2,0) node[label={left:$V_1$}] {}
					(opamp.+) to [R, l^=$R_2$] ++(0,2) node[ground,rotate = 90]{}
					(opamp.-) -- ++(0,-1.7) -- ++(0.5,0)
					to [R, l^=$R_2$] ++(1.5,0) -- ++(0.4,0) to (opamp.out)
					(opamp.out) -- ++(1,0) to [open,v=$V_2$,o-o] ++(0,-3) node[ground]{};
			
				\end{circuitikz}
			\end{figure}

			\[
			V_2 = \frac{R_1}{R_1}(V_1 - V_{dac1})
			\]

			यदि, $R_1 = 10K$,
			
			\[
			V_2 \approx V_1 - V_{dac1}
			\]

		\subsubsection{प्रोग्रामेबल एम्पलीफायर}
		
			सिगनल को बढ़ाना आवश्यक हो जाता है क्योंकि त्वचा की टोन, सेंसर के साथ अनुचित उंगली संपर्क या किसी भी त्वचा रंजकता\cite{skin} से सिगनल में क्षीणन होता है। यह चरण चयन योग्य परिवर्तनीय लाभ प्रदान करता है जिसे माइक्रोकंट्रोलर द्वारा निर्धारित किया जा सक़ता है।
			
			$\mu$C निर्धारित करेगा कि किस स्तर के प्रवर्धन की आवश्यकता है और संबंधित सिगनल पिन को उच्च ड्राइव करेगा ताकि संबंधित अवरोध चयनित हो जाए।

			\begin{figure}[ht!]\centering
				\begin{circuitikz}[american] 
					\draw
						(2,3) node[op amp,yscale=-1] (opamp) {}
						(opamp.down) -- +(0,0.3) node[vcc]{Vcc}
						(opamp.up) -- +(0,-0.3) node[ground]{}
						(opamp.+) to ++(-2,0) node[label={left:$V_2$}] {}
						(opamp.-) -- ++(0,-1.7) -- ++(1,0)
						to [R, l^=$10K$] ++(1,0) -- ++(1,0) -- ++(0,2.2) to (opamp.out)
						(opamp.-) ++(0,-1.7) -- ++(0,-1.5) to [R, l^=$10K$] ++(0,-1) -- ++(0,-0.5)
						++(0,-0.5) node[npn] (Q1){}
						(Q1.E) node[ground]{}
						(Q1.B) to [R, l^=$4.7K$] ++(-1.5,0) node[label={left:S1}] {}
						
						(opamp.-) ++(0,-1.7) ++(0,-0.75) -- ++(3.5,0) -- ++(0,-0.75)		
						to [R, l^=$4.7K$] ++(0,-1) -- ++(0,-0.5)
						++(0,-0.5) node[npn] (Q2){}	
						(Q2.E) node[ground]{}	
						(Q2.B) to [R, l^=$4.7K$] ++(-1.5,0) node[label={left:S2}] {}
						
						(opamp.-) ++(0,-1.7) ++(0,-0.75) ++(2,0) -- ++(5,0) -- ++(0,-0.75)		
						to [R, l^=$2.35K$] ++(0,-1) -- ++(0,-0.5)
						++(0,-0.5) node[npn] (Q3){}	
						(Q3.E) node[ground]{}	
						(Q3.B) to [R, l^=$4.7K$] ++(-1.5,0) node[label={left:S3}] {};

				 \end{circuitikz}
			\end{figure}	
	
			\begin{center}
				\begin{tabular}{ |c|c|} 
					\hline
					\textbf{स्विच} & \textbf{बढ़त}   \\ 
					\hline
					सभी बंद & 1 	 \\ 
					\hline
					S1 & 2  		\\ 
					\hline
					S2 & 3  		\\ 
					\hline
					S1+S2 & 4  		\\ 
					\hline
					S3 & 5  		\\ 
					\hline
					S1+S3 & 6	  	\\ 
					\hline
					S2+S3 & 7  		\\ 
					\hline
				\end{tabular}
			\end{center}

	\subsection{LED चालक}

		जैसा कि पहले चर्चा की गई थी, ट्रांस्इम्पेडेंस चरण के बाद सिगनल स्तर बहुत कम हो सकता है। led ड्राइवर को आवश्यकतानुसार led के केरंट बढ़ाना की जरूरत है। निम्नलिखित सर्किट का उपयोग वोल्टेज नियंत्रित करंट स्रोत के रूप में किया गया है, वोल्टेज को DAC सेट करता है $\mu$C के निर्देशन पे।
		
		\begin{figure}[ht!]\centering
			\begin{circuitikz}[american] 
				\draw
				
				(4,3) node[npn] (Q1){}
				(Q1.E) to [R, l^=20] ++(0,-1.5) node[ground]{}
				(Q1.B) to [R, l^=4.7K] ++(-1.5,0) node[label={left:$V_{dac2}$}] {}
				(Q1.C) -- ++(-1,0) -- ++(0,0.5) ++(0,0.5)  node[npn] (Q2){}
				(Q2.B) to [R, l_=10K] ++(-1.5,0) node[label={left:Red pulse}] {}
				(Q2.C) -- ++(0,1) node[]{} ++(0,0.2) node[]{Red cathode}
				(Q1.C) -- ++(1,0) -- ++(0,0.5) ++(0,0.5) node[npn,xscale=-1] (Q3){}
				(Q3.B) to [R, l^=10K] ++(1.5,0) node[label={right:IR pulse}] {}
				(Q3.C) to ++(0,1) node[]{} ++(0,0.2) node[]{Ir cathode};
			\end{circuitikz}
		\end{figure}

		जब भी लाल/इन्फ्रारेड पल्स सक्रिय होता है, तो led एकल पुल विन्यास द्वारा सक्रिय हो जाते हैं, संबंधित लाल/इन्फ्रारेड led सक्रिय हो जाते हैं (Vcc से जुड़े led एनोड)। करंट की मात्रा $V_{dac2}$ \& $R_1$ पर निर्भर करेगी।
		
		$V_{dac2}$ भी स्पंदित आवृत्ति के अनुसार लाल और इन्फ़्रारेड के लिए अलग-अलग सेट किया जायेगा। यदि सिग्नल का पता लगाने के लिए तीव्रता पर्याप्त नहीं हो, तो $V_{dac2}$ को बढ़ाना आवश्यक है। $\mu$C थ्रेसहोल्ड का निर्धारण करेगा और उसके अनुसार नियंत्रण वोल्टेज को संशोधित करेगा।	

		प्रोग्रामेबल एम्पलीफायर चरण के बाद अंतिम आउटपुट नीचे दिखाया गया है। प्राप्त PPG सिग्नल - लाल और इन्फ़्ररा-रेड स्पष्ट रूप से दिखाई दे रहे है और एक उपयुक्त स्तर पर है जिसे ADC को भेजा जा सक़ता है ऐल्गोरिद्म मे उपयोग के लिये। 
	
	\begin{figure}[ht!]
		\centering
		\subfloat[अंतिम आउटपुट - हरा, V\textsubscript{1} - नीला
		]{}
		\hfill
		\subfloat[अंतिम आउटपुट का माप
		]{}
		\caption{अंतिम आउटपुट}
	\end{figure}

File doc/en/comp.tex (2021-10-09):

\section{Main System Components}

	\subsection{Photodiode}
	
		Photodiode will be used as a detector in a reflective configuration, wherein light is projected from one end using LEDs and photodiode is detecting light at the opposite end converting it to current. This current would be proportional to LEDs brightness.

		\begin{figure}[ht!]
			\centering
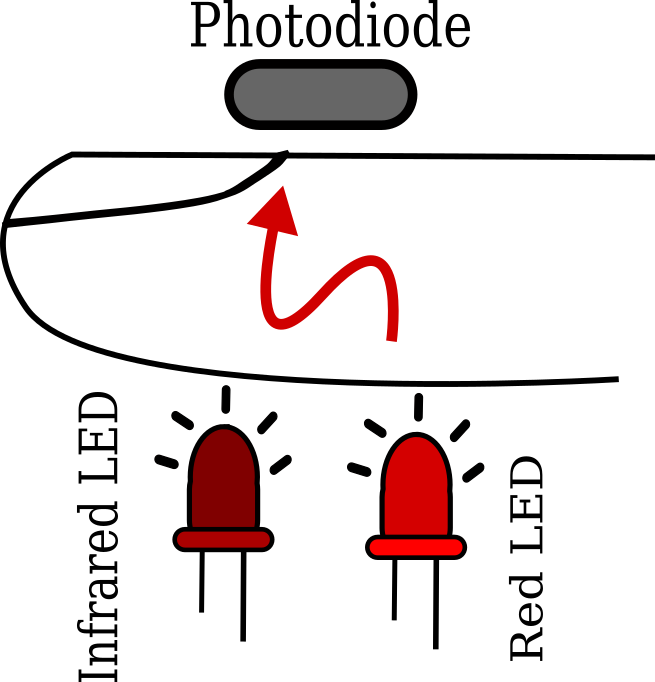
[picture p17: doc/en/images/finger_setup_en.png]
			
			\caption{Reflective finger setup}
		\end{figure}

		Photodiode needs to be sensitive in both red (700nm) and infrared (900nm) regions. QSB34CGR was used in this design which can work in both regions as seen in the sensitivity graph from part's datasheet.
	
		\begin{figure}[ht!]
			\centering
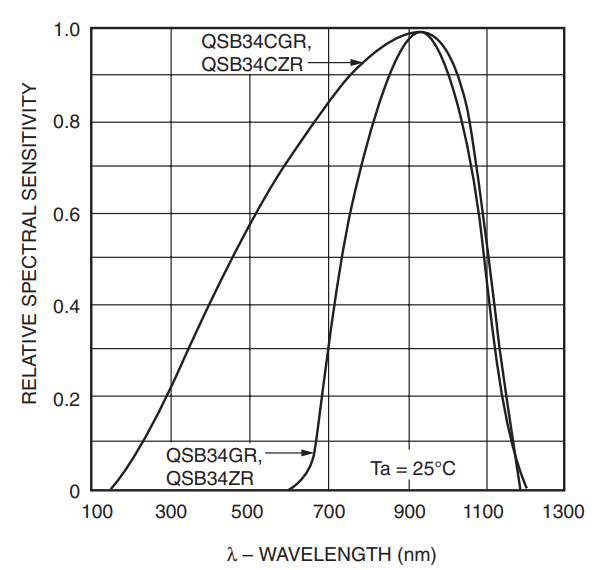
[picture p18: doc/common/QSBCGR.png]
			
			\caption{QSB34CGR sensitivity spectrum}
		\end{figure}
	
	\pagebreak
	
	\subsection{Microcontroller}
	
		Microcontroller($\mu$C) is responsible for the algorithm in calculating the SpO\textsubscript{2} by reading the red and ir amplified channels via ADC. Also it performs the following tasks:
		
		\begin{itemize}
			\item Interfaces with an OLED 128x64 display to show the calculated  SpO\textsubscript{2} and heart beat.
			
			\item Interfaces with DACs.
		\end{itemize}
		
		Atmega4808 is used in this design.
	
	\subsection{Dual DAC}
	
		Dual digital to analog converter - MCP47FEB02A0 was used in design.
		
		\begin{itemize}
			
			\item DAC1 is required in LED driver stage so that $\mu$C can instruct the DAC to generate a required control voltage to set led current.
			
			\item DAC2 provides an input to the difference amplifier stage for DC removal from signals.
		
		\end{itemize}
		
	\subsection{Leds}
		It is important to select good leds for illumination, following factors ensure good signal response:
		
		\begin{itemize}
			\item Narrow view angle for less dispersion and deeper penetration into skin.
			\item Rectangular package in clear lens so that finger can rest comfortably.
			\item High radiant power.
		\end{itemize}
	
		I didn't get new leds and worked with generic 3mm/5mm ir led in circular clear package and a red led in diffused package. This caused the R ratio to not be correct. As a healthy individual, i was getting readings of R to be around 0.6 while it should be around 0.4. So I had to use a scaling factor to adjust the algorithm. A comment has been added in the program code regarding this. 
		
		A suitable choice can be Vishay Semiconductor's VSMD66694.

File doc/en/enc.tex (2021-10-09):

\section{PCB \& Enclosure}

	\subsection{PCB}	
	
		\begin{figure}[ht!]
			\centering
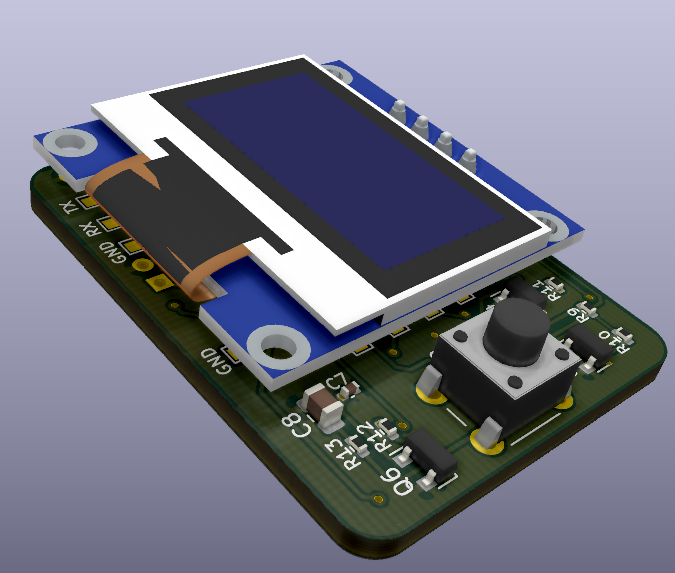
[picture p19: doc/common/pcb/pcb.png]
			
			\caption{Completed PCB}
		\end{figure}

		\begin{figure}[ht!]
			\centering
			\subfloat[PCB Back
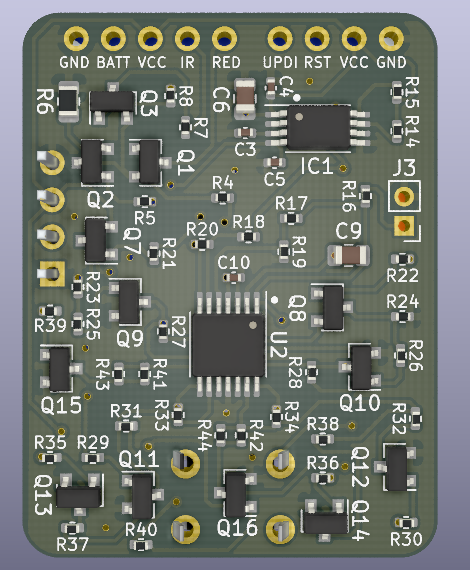
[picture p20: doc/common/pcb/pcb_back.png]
			]{}
			\hfill
			\subfloat[PCB Front
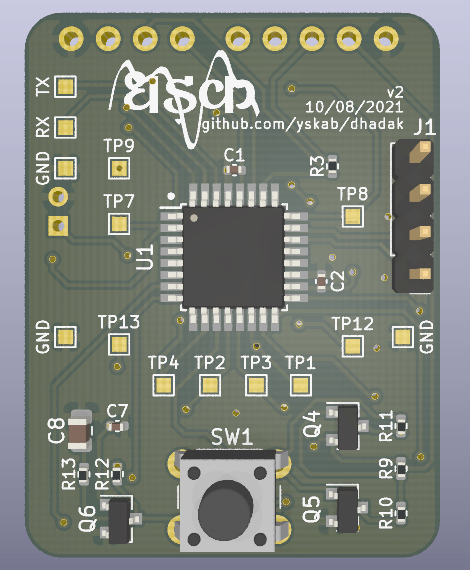
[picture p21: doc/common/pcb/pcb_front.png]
			]{}
			\caption{PCB Images}
		\end{figure}

		PCB Design was completed on 2 layers with most of the components placed on the back side so that they can be re-flowed easily on a dosa pan. All components on front side are to be hand soldered.
		
		\begin{itemize}
			
			\item Design also includes a soft latch power on/off switch circuit to easily operate the device.
			
			\item A programming header was also added to program the $\mu$C via UPDI interface.
			
			\item Connection headers were added to connect the leds, battery \& photodiode which will be present on bottom compartment of enclosure.
			
			\item Header to attach OLED Display.

		\end{itemize}
	
		Sufficient test points were added on front side for easy access to probe and view the signals on oscilloscope.
		
		To keep the PCB size equivalent to that of the OLED display module, 0402 size resistors/capacitors were used.

	\subsection{Enclosure}		
		
		Enclosure was designed taking reference from a typical Oximeter which has display \& PCB on top, a finger insert below and a bottom part with battery compartment.
		
		\begin{figure}[ht!]
			\centering
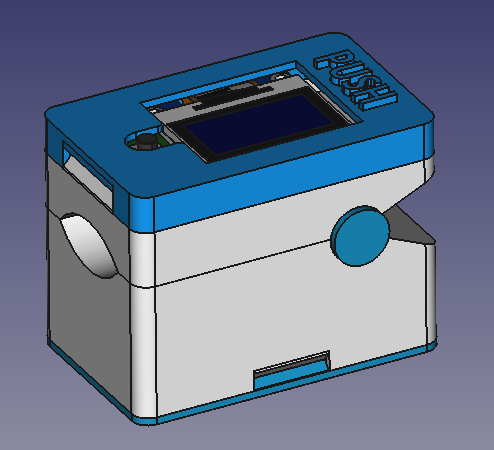
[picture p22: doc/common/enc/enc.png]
			
			\caption{Completed Enclosure}
		\end{figure}	

		A reflective setup was implemented with photodiode on top base and pulse leds in bottom compartment. 
				
		\begin{figure}[ht!]
			\centering
			\subfloat[Photodiode compartment
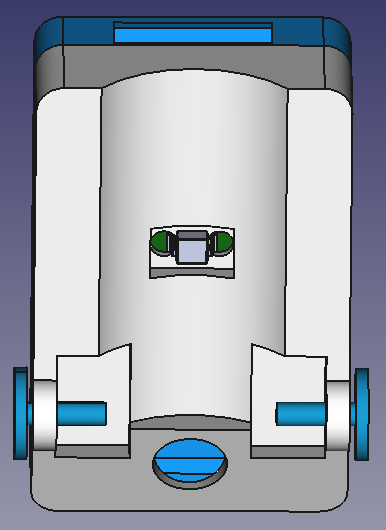
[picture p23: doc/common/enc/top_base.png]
			]{}
			\hfill
			\subfloat[Spacers for pcb
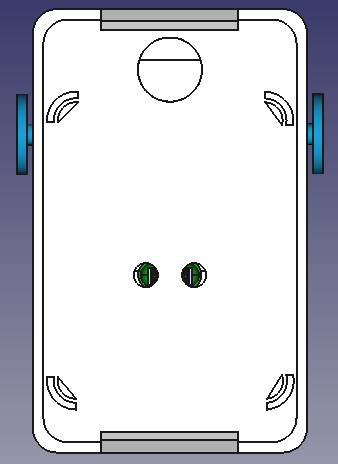
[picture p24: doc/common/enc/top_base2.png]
			]{}
			\caption{Top Base}
		\end{figure}

		\begin{figure}[ht!]
			\centering
			\subfloat[Battery compartment
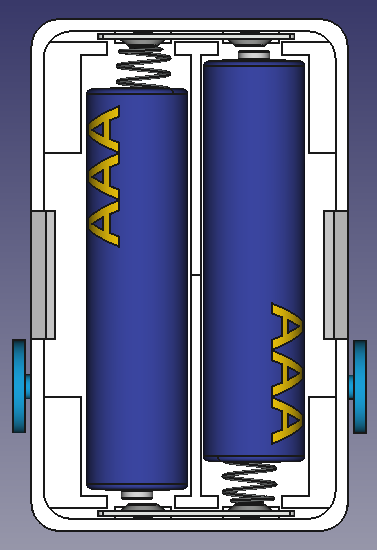
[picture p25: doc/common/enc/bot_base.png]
			]{}
			\hfill
			\subfloat[Led compartment
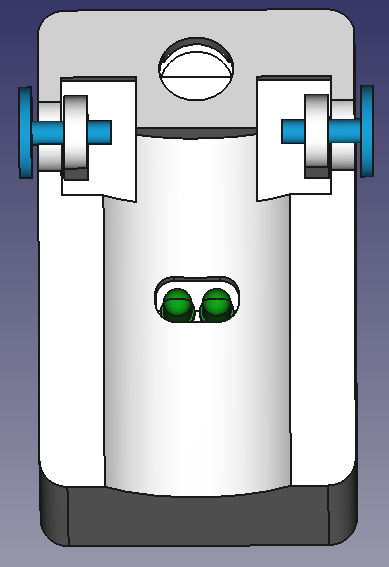
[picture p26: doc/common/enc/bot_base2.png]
			]{}
			\caption{Bottom Base}
		\end{figure}

		Securing finger is an important part as any wobble or improper contact would lead to degradation in signal quality and calculated parameters. To achieve a firm pressure onto the finger which would hold it stable in place, a safety pin was used (removing the clip part) in the rotation mechanism.
		
		\begin{figure}[ht!]
			\centering
			\subfloat[Safety pin
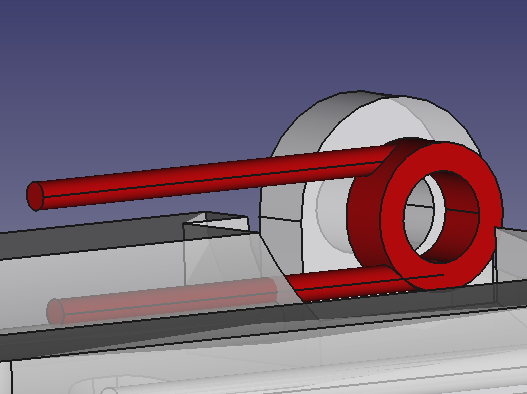
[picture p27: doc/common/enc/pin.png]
			]{}
			\hfill
			\subfloat[Side view of pin
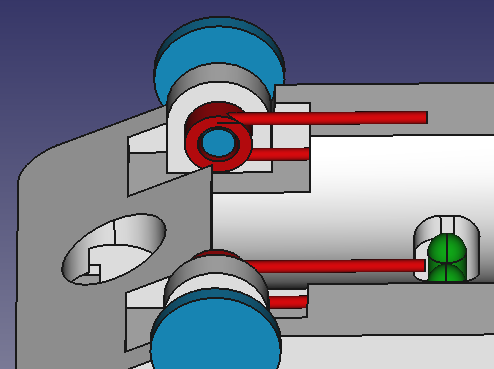
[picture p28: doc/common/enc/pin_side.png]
			]{}
			\caption{Pin mounted in bottom base}
		\end{figure}	
		
		In idle position, pin would be in natural non-extended state hence both base parts would be closed. When a finger is inserted, lid needs to go up via the rotational mechanism as that is the only path to accommodate the finger. This would cause the upper part connected with pin to push down on finger which would lead to a firm grip to form ensuring good contact with photodiode and led.

		\begin{figure}[ht!]
			\centering
			
			\caption{Snap fit cross-section}
		\end{figure}	

		Snap fit elements were implemented making it easier to fit and remove the cover parts whenever required.

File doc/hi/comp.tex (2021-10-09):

\section{मुख्य इलेक्ट्रानिक उपकरण}

	\subsection{फोटोडायोड}
	
		फोटोडायोड का उपयोग एक परावर्तक विन्यास में एक डिटेक्टर के रूप में किया जाएगा, जिसमें LED एक छोर से प्रकाश उत्सर्जित करते है और फोटोडायोड विपरीत छोर पर प्रकाश को करंट में परिवर्तित कर रहा है। यह करंट LED प्रकाश की तीव्रता के समानुपाती होगा।
		
		\begin{figure}[ht!]
			\centering
			
			\caption{चिंतनशील उंगली सेटअप}
		\end{figure}

			इस डिज़ाइन मे फोटोडायोड QSB34CGR का उपयोग किया गया है। देखा जा सकता है, चयनित फोटोडायोड लाल (700nm) और इन्फ्रा-रेड (900nm) क्षेत्रों में संवेदनशील है, इसलिए दोनों स्रोतों को बारी-बारी से प्रकाशित करके विद्युत-धारा तीव्रता मापी जा सकती है।
		\begin{figure}[ht!]
			\centering
			
			\caption{QSB34CGR स्पैक्ट्रम संवेदनशीलता}
		\end{figure}
	
	\pagebreak
	
	\subsection{माइक्रोकंट्रोलर}
	
		माइक्रोकंट्रोलर($\mu$C) ADC के माध्यम से लाल और इन्फ्रा-रेड प्रवर्धित सिग्नल को पढ़कर SpO\textsubscript{2} की गणना के ऐल्गोरिद्म के लिए जिम्मेदार है। इसके अलावा यह निम्नलिखित कार्य करता है:
		
		\begin{itemize}
			\item गणना की गई SpO\textsubscript{2} और दिल की धड़कन दिखाने के लिए OLED 128x64 डिस्प्ले के साथ इंटरफेस।
			
			\item DACs के साथ इंटरफेस। 
			
		\end{itemize}
		
		इस डिज़ाइन में Atmega4808 का उपयोग किया गया है।
	
	\subsection{दोहरी DAC}

		दोहरी डिजिटल से एनालॉग कनवर्टर (DAC) - MCP47FEB02A0 डिजाइन में उपयोग किया गया है।
		
		\begin{itemize}
			
			\item DAC1 की आवश्यकता है ताकि $\mu$C DAC को LED करंट सेट करने के लिए आवश्यक नियंत्रण वोल्टेज उत्पन्न करने का निर्देश दे सके।
			
			\item DAC2 सिगनल से DC को हटाने के लिए डिफ़ैंस एम्पलीफायर चरण के लिए एक इनपुट प्रदान करता है।
		
		\end{itemize}
	
	\subsection{Leds}
		रोशनी के लिए अच्छे led का चयन करना महत्वपूर्ण है, निम्नलिखित कारण अच्छी सिग्नल प्रतिक्रिया सुनिश्चित करते हैं:
				
		\begin{itemize}
			\item कम फैलाव और त्वचा में गहरी प्रवेश के लिए संकीर्ण दृश्य कोण। 
			\item क्लियर lens समकोण पैकेज - ताकि उंगली आराम से led पर बैठ सकें। 
			\item उच्च दीप्तिमान शक्ति। 
		\end{itemize}
		
		मैने 3mm/5mm कि सामान्य leds का उपयोग किया। 5mm कि इन्फ़्ररेड led सर्कुलर क्लियर पैकेज में और 5mm डिफ्यूज्ड पैकेज में लाल led का इस्तेमाल किया डिजाइन मे। इसके कारण R अनुपात सही नहीं हो रहा था। एक स्वस्थ व्यक्ति के रूप में, मुझे R की रीडिंग 0.6 के आसपास मिल रही थी, जबकि यह 0.4 के आसपास होनी चाहिए। इसलिए मुझे ऐल्गोरिद्म को समायोजित करने के लिए स्केलिंग कारक का उपयोग करना पड़ा। इस संबंध में प्रोग्राम कोड में एक कमेंट लिखा गया है। 
		
		Vishay Semiconductor VSMD66694 एक उपयुक्त led हो सकती है आक्सीमीटर के लिये।

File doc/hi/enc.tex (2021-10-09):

\section{पीसीबी व एन्क्लोज़र}

	\subsection{पीसीबी}	
	
		\begin{figure}[ht!]
			\centering
			
			\caption{पूर्ण पीसीबी}
		\end{figure}

		\begin{figure}[ht!]
			\centering
			\subfloat[पीसीबी पिछ्ला भाग
			]{}
			\hfill
			\subfloat[पीसीबी अग्र भाग
			]{}
			\caption{पीसीबी के चित्र}
		\end{figure}

		पीसीबी डिजाइन को 2 परतों पर पूरा किया गया था जिसमें अधिकांश अंशो को पीछे की तरफ रखा गया था ताकि उन्हें डोसा पैन पर आसानी से री-फ़्लो किया जा सके। सामने की तरफ के सभी अंशो को हाथ से सोल्डर किया जाना है। 

		\begin{itemize}
			
			\item डिवाइस को संचालित करने के लिए एक सॉफ्ट लैच पावर ऑन/ऑफ स्विच सर्किट भी शामिल है।
			
			\item UPDI इंटरफ़ेस के माध्यम से $\mu$C को प्रोग्राम करने के लिए एक प्रोग्रामिंग हेडर भी लगाया गया था।
			
			\item Led, बैटरी और फोटोडायोड को जोड़ने के लिए कनेक्शन हेडर बनाये गए है जो एन्क्लोज़र के निचले हिस्से पर मौजूद होंगे।
			
			\item OLED डिस्प्ले के लिये हैडर। 

		\end{itemize}
	
		जांच के लिए आसान पहुंच और ऑसिलोस्कोप पर संकेतों को देखने के लिए सामने की तरफ पर्याप्त परीक्षण बिंदु जोड़े गए थे।
		
		पीसीबी साइज को OLED डिस्प्ले मॉड्यूल के बराबर रखने के लिए 0402 साइज रेसिस्टर्स/कैपेसिटर का इस्तेमाल किया गया।

	\subsection{एन्क्लोज़र}		
		
		एन्क्लोज़र को एक सरल ऑक्सीमीटर से संदर्भ लेते हुए डिज़ाइन किया गया था जिसमें शीर्ष पर डिस्प्ले \& PCB, निचला भाग पर फिंगर इंसर्ट और बैटरी कंपार्टमेंट है।
		
		\begin{figure}[ht!]
			\centering
			
			\caption{पूर्ण एन्क्लोज़र}
		\end{figure}	
				
		उपरि भाग पर फोटोडायोड और निचले में led एक चिंतनशील सेट अप मे मौजूद है। 
				
		\begin{figure}[ht!]
			\centering
			\subfloat[फोटोडायोड कम्पार्टमेंट
			]{}
			\hfill
			\subfloat[पीसीबी के लिए स्पेसर
			]{}
			\caption{उपरि भाग}
		\end{figure}

		\begin{figure}[ht!]
			\centering
			\subfloat[बैटरी कम्पार्टमेंट
			]{}
			\hfill
			\subfloat[Led कम्पार्टमेंट
			]{}
			\caption{निचला भाग}
		\end{figure}
	
		उंगली को सुरक्षित करना एक महत्वपूर्ण हिस्सा है क्योंकि किसी भी तरह के डगमगाने या अनुचित संपर्क से सिग्नल की गुणवत्ता और गणना किए गए मापदंडों में गिरावट आ सकती है। उंगली पर एक मजबूत दबाव प्राप्त करना जरुरी है जो इसे स्थिर रखेगा, इसीलिये रोटेशन तंत्र में एक सेफ्टीपिन (क्लिप भाग को हटाकर) का उपयोग किया गया है।
		
		\begin{figure}[ht!]
			\centering
			\subfloat[सेफ्टीपिन
			]{}
			\hfill
			\subfloat[सेफ्टीपिन का द्र्शय
			]{}
			\caption{सेफ्टीपिन निचले भाग मे}
		\end{figure}	
		
		निष्क्रिय स्थिति में, सेफ्टीपिन (पिन) प्राकृतिक गैर-विस्तारित अवस्था में होगा इसलिए दोनों  भाग बंद हो जाएंगे। जब उंगली डाली जायेगी, उपरि हिस्से को उठना होगा रोटेशन तंत्र के माध्यम से जभी उंगली अंदर जाएगी। इस से पिन उपरी भाग को उंगली पर नीचे धकेलेगा जिससे फोटोडायोड के साथ अच्छा संपर्क सुनिश्चित होगा और एक मजबूत पकड़ बनेगी। 

		\begin{figure}[ht!]
			\centering
			
			\caption{स्नैप फिट क्रॉस-सेक्शन}
		\end{figure}	

		स्नैप फिट तत्वों को लागू किया गया है जिससे जब भी आवश्यक हो कवर भागों को फिट करना और निकालना आसान हो सके।

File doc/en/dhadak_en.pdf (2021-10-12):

### English

During the COVID-19 wave in India, I saw a lot of people buying oximeters from medical stores and online to monitor oxygen levels at home. I was quite intrigued, how can a small device plugged to a finger could calculate heart rate and oxygen saturation? This question got me started to research and understand how these things actually work and whether I can make one from scratch. In the process I realized, it would be helpful to write all details in an understanding document which will serve as a memory to me and can be of help to others too. Also, I wanted to start learning LATEX so as to create beautiful written documents for all future projects.

This writing tries to present a brief theory of what oximetery is, how electronic components can be used to get the oxygen saturation value and heart rate. Required circuit block elements and algorithms have also been discussed. It has been assumed that reader has knowledge of:

- Basic circuit analysis & electronic components
- Opamp & transistor working

I am a beginner in my electronics journey, hence there can be mistakes in this article. The accuracy of information presented has not been inspected by any other person than myself. This guide was written so that it can become a source of knowledge to anyone trying to understand how to make an oximeter or how oximeter works. Presented design is not be used in any life support systems.

This document was written in TexStudio editor.

All pictures have been produced with Inkscape.

Plots were generated in GNU Octave.

PCB & Schematics designed using Kicad.

Enclosure was designed in FreeCAD.

All project related files are at: https://github.com/yskab/dhadak

Video series: https://youtu.be/QoOAn5z_qHc

For reporting any mistakes or corrections raise an issue on Github.

You can reach me on Twitter for posts and messages @yskabhijeet (https://twitter.com/yskabhijeet)

### Y S K Abhijeet

October 12, 2021

i

### Contents

1 Introduction | 1
1.1 Cardiac Cycle | | 1
1.2 Oximetry Principle | | 1
2 Main System Components | 7
2.1 Photodiode | | 7
2.2 Microcontroller | | 8
2.3 Dual DAC | | 8
2.4 Leds | | 8
3 Circuit Design | 9
3.1 Front End | | 9
3.1.1 | Transimpedance Stage | | 9
3.1.2 | Difference Amplifier | 11
3.1.3 | Programmable Gain Amplifier | 13
3.2 LED Driver | 14
4 Algorithm | | 16
4.1 IIR Filter | 17
4.2 Heart Rate | 18
4.3 SpO2 Calculation | 19
5 PCB & Enclosure | 21
5.1 PCB | 21
5.2 Enclosure | 22
6 References | | 25
7 Closing Comments | 26

ii

### 1 Introduction

Oximetry is the process of measuring the concentration of oxygen in blood (oxygen saturation - SpO2). Normal levels of SpO2 should usually be around 95% to 100%, level below 90% could lead to Hypoxemia which can cause shortness of breath and headache¹

### 1.1 Cardiac Cycle

Red blood cells contain Hemoglobin, a protein which when comes in contact with fresh oxygen via lungs forms Oxygenated Hemoglobin (HbO2). This Oxygenated blood is carried from the lungs to left side of the heart, which pumps this blood around the body through arteries. The cells of the body convert the chemical energy from oxygen molecules in red blood cells into Adenosine Triphosphate (ATP). ATP is stored in the cell and can be used for organism’s life support system as required. Absence of oxygen in red blood cells due to conversion into ATP forms Deoxygenated Hemoglobin (Hb).

This deoxygenated blood returns through the veins to right side of the heart, from there the blood is pumped into lungs to expel carbon dioxide and again fresh oxygen is inhaled and blood gets oxygenated. This completes a single Cardiac Cycle.

### 1.2 Oximetry Principle

Pulse Oximeter is based on PPG (Photoplethysmography) wherein a light source is projected and a detector is used to measure volumetric changes in blood. It has been observed that Hb has a higher absorption when red wavelength is passed through while HbO2 has a higher absorption towards infrared wavelength source (Figure 1). If we can relate the detected output with concentration of Hb/HbO2 in blood, a relation can be obtained to calculate SpO2.

Heart pumps blood with each cardiac cycle and this leads to change in blood volume in the artery. When light is passed through (finger, earlobe, wrist[1] depending on it’s wavelength, Hb/HbO2 components will also get absorbed and PPG signal is obtained as an output. Signal peaks correspond to completion of a cardiac cycle (heart

1https://www.mayoclinic.org/symptoms/hypoxemia/basics/definition/sym-20050930

1


Figure 1: Absorption Spectra - Hb/HbO2


Figure 2: PPG waveform when a single light source is projected

beat). This varying signal also has a DC level due to absorption of light source by skin, venous blood and tissue.

From this understanding, if we can find molecular concentrations of Hb and HbO2 in a defined blood volume, SpO2 can be calculated as a ratio of oxygenated blood concentration to total concentration:

SpO2 =

HbO2
Hb + HbO2

(1)

According to Beer-Lambert law:

log10

I
Io
= lc | (2)

2

I− Transmitted light intensity

Io− Incident light intensity

l− length

c− Molecular concentration

− Molar absorption coefficient


Figure 3: Light source projected onto a finger

As seen in Figure 3, a light source is projected onto a finger and transmitted light is detected on the other end. Infrared and Red light is pulsed individually. For infrared source:

c1 =

log10

I1
Io1
1l

Since HbO2 has higher absorption for infrared wavelength,

HbO2 =

log10

I1
Io1
1l

Similarly for red,

Hb =

log10

I2
Io2
2l

According to (1),

SpO2 =

log10

I1
Io1
1l

log10

I2
Io2
2l +

log10

I1
Io1
1l

if R =

log10

I2
Io2
log10

I1
Io1

,

3

SpO2 =

1
1
R
2

+

1
1

SpO2 =

2
R1 + 2

(3)

SpO2 mostly depends on R, we can consider calculating R and later comparing with a calibrated reference to get the actual SpO2.

Since Incident light intensity level would be constant while pulsed, R would depend only upon I1 and I2,

R ≈

log10 I2
log10 I1

≈

I2
I1

≈

AC2
AC1

We need not calculate the logarithm, as the actual SpO2 would be obtained from a Look up table or an empirical equation which demonstrates relation of R to SpO2. Standard oximeter manufacturers would test their device on large group of subjects and obtain the R values and subject’s actual SpO2 using a separate calibrated meter to prepare a relationship curve. Once this mapping is obtained, SpO2 for any subject can be calculated using the relationship.

SpO2%

Figure 4: A typical relationship curve R vs SpO2

Since detected IR and Red signals can have varying DC levels, we need to normalize the ratio first by dividing the DC levels so that a direct comparison of the PPG (AC component) can be performed

4

as that caries the absorbed/un-absorbed information, hence R now becomes:

R = AC2
DC2

/

AC1
DC1
(a) Before Normalization


(b) After Normalization

Figure 5: Effect of Normalization

R = Vp2 − Vl2
DC2

/

Vp1 − Vl1
DC1

(4)

As shown in Figure 5,

Vp1− Ir Peak

Vl1− Ir Valley

Vp2− Red Peak

Vl2− Red Valley

DC1− Ir DC level

DC2− Red DC level

5

This value of R when compared with relationship curve would give the actual SpO2.

We can consider calculating R for a set of samples and average them, instead of waiting for peaks and valleys to arrive. In this implementation, R is calculated between neighboring samples and a weighted average[9] is calculated for final value. This is discussed further in SpO2 calculation algorithm section.

6

### 2 Main System Components

### 2.1 Photodiode

Photodiode will be used as a detector in a reflective configuration, wherein light is projected from one end using LEDs and photodiode is detecting light at the opposite end converting it to current. This current would be proportional to LEDs brightness.

Figure 6: Reflective finger setup

Photodiode needs to be sensitive in both red (700nm) and infrared (900nm) regions. QSB34CGR was used in this design which can work in both regions as seen in the sensitivity graph from part’s datasheet.


Figure 7: QSB34CGR sensitivity spectrum

7

### 2.2 Microcontroller

Microcontroller(µC) is responsible for the algorithm in calculating the SpO2 by reading the red and ir amplified channels via ADC. Also it performs the following tasks:

- Interfaces with an OLED 128x64 display to show the calculated SpO2 and heart beat.
- Interfaces with DACs.

Atmega4808 is used in this design.

### 2.3 Dual DAC

Dual digital to analog converter - MCP47FEB02A0 was used in design.

- DAC1 is required in LED driver stage so that µC can instruct the DAC to generate a required control voltage to set led current.
- DAC2 provides an input to the difference amplifier stage for DC removal from signals.

### 2.4 Leds

It is important to select good leds for illumination, following factors ensure good signal response:

- Narrow view angle for less dispersion and deeper penetration into skin.
- Rectangular package in clear lens so that finger can rest comfortably.
- High radiant power.

I didn’t get new leds and worked with generic 3mm/5mm ir led in circular clear package and a red led in diffused package. This caused the R ratio to not be correct. As a healthy individual, i was getting readings of R to be around 0.6 while it should be around 0.4. So I had to use a scaling factor to adjust the algorithm. A comment has been added in the program code regarding this.

A suitable choice can be Vishay Semiconductor’s VSMD66694.

8

### 3 Circuit Design

Photodiode; RED LED; IR LED; LED Driver; Transimpedance Amplifier; Difference Amplifier; Programmable Gain Amplifier; µC ADC µC

Figure 8: System Block Diagram

Referring the Block diagram, subsections are divided below that show the circuit and corresponding oscilloscope trace outputs.

### 3.1 Front End

### 3.1.1 Transimpedance Stage

Photodiode’s current is needed to be converted to a proportional voltage so that ultimately the microcontoller can convert the voltage to a digital value using an ADC for calculation of SpO2. A simple Transimpedance Amplifier configuration was used to achieve this:

As per led’s intensity, if a current of 10µA is produced in the photodiode, and R = 100KΩ, according to Ohm’s law, V1 = 1 V. Capacitor

9

is used for low-pass filtering of the pulse. Cut off frequency would be:

Fc =

1
2πR1C1

(5)

If R1=576KΩ, C1 = 33pF,

Fc ≈ 8.3 kHz


(a) V1


(b) V1 zoomed in

Figure 9: V1 Oscilloscope trace (Red & IR pulsed sequentially)

10

Since LEDs are pulse on-off at a fast rate sequentially the pulse would look like a square wave. We need to use a pulse frequency less than 1/10th of this cut-off to pulse the LEDs so that the square wave with all its high-frequency components is clearly visible and not filtered out.

Fp = 500 Hz

It can be seen in traces, 2 PPG signals are observable, riding on a DC level. Higher amplitude one is a result of ir led pulsing, while lower amplitude is from red led. Since the peaks correspond to heart rate, in this case as per trace, it measures out to be 1.42/sec or 85BPM. Individual pulses which construct the signal can be seen in Figure 9b. Amplitude of detected red signal is lower than ir and that is due to:

- Higher intensity of ir led due to higher ir current.
- Photodiode’s red sensitivity is 80% of ir sensitivity.
- Ir penetrates into skin deeper than red, hence a better ir response is visible at photodiode[2].

Hence to obtain a suitable response, it is important to increase led intensity until it reaches a required level so that the PPG signal has a higher amplitude.

### 3.1.2 Difference Amplifier

PPG signal needs to be amplified to a suitable level so that full scale ADC range can be utilized to better digitize the signal. Right now, amplitude of PPG signal is quite low and DC level is higher. We are not bothered by the DC anymore, µC can read it and store for R value calculation, we only need to amplify the AC part which is an envelope of the signal. Direct amplification would lead to gain of the DC level as well, as the required signal is riding on top of it. This will saturate the opamp and amplification level range will be quite low.

If we can subtract the DC level from entire signal, only AC would remain which can be easily amplified further at higher levels. A Difference amplifier along with a 8bit Digital to analog converter (DAC) generating the DC cancellation signal can be used here. Since red and ir have different levels, separate DC levels are generated by DAC in sync with the pulsed frequency.

11


Figure 10: Effect of Difference Amplifier

As shown in Figure 10 a plot generated in Octave demonstrates subtraction of required signal and diff signal. This difference can then be amplified further. Pulse width of diff signal is slightly larger than required signal so that there are no spikes on edges in output signal. Also the lower level of diff signal is slightly above 0V to allow the difference to always be negative in low states and since negative supply is grounded, output would be 0V here.

Vcc; Vdac1

V2 =

R1
R1

(V1 − Vdac1)

12

For R1 = 10K,

V2 ≈ V1 − Vdac1

### 3.1.3 Programmable Gain Amplifier

It becomes necessary to amplify the signal as skin tone, improper finger contact with sensor or any skin pigmentation[3] can cause attenuation in signal leading to low amplitudes. This stage provides selectable variable gain which can be set by microcontroller.

µC would determine what level of further amplification is required and drive the respective pin high so that resistor value would get

S1 | 2
S2 | 3
S1+S2 | 4
S3 | 5
S1+S3 | 6
S2+S3 | 7

13

### 3.2 LED Driver

As discussed previously, the detected signal levels can be very low after I to V stage. LED Driver needs to increase current to the leds as required. Following circuit is used as a voltage controlled current source, voltage is set by the DAC as instructed by the µC.

Vdac2; Red pulse; Red cathode; IR pulse; Ir cathode

Leds get activated by a single bridge configuration, whenever red/ir pulse is active, corresponding red/ir leds get active (led anodes connected to Vcc). Amount of current would depend on Vdac2 & R1.

Vdac2 is also set individually for red and ir as per the pulsed frequency. If intensity is not sufficient for signal detection, it is necessary to increase Vdac2. µC would determine the thresholds and modulate the control voltage accordingly.

Shown below is final output after the PGA stage. The gained up PPG signal is clearly visible for both red and ir which is at a suitable level for ADC capture and usage in algorithms for calculations.

14


(a) Final output - green, V1 - blue


(b) Final output measurement

Figure 11: Final output

15

### 4 Algorithm

Start; Pulse leds; Wait 0.5 secs; V1 within preset levels Set new drive current; Find red/ir DC levels; Generate Diff signal; V2 within preset level; PGA: Select gain & Amplify; Read ADCs at every pulse; nd order IIR filter; Detect; Peaks & valley; Calculate HR; Calculate R Ratio; Average &; Calculate SpO2; False; True; red\ir leds pulsed; sequentially at 500 Hz; wait 0.5 secs for; PPG signal to settle; check if PPG signal; within acceptable levels; else inc/dec drive current; determine red & ir; dc levels to generate; diff signal; DAC generates diff signal; for DC subtraction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

Figure 12: Program Flow

16

### 4.1 IIR Filter

ADC read samples can have little noise spikes which if passed directly to peak-valley detect function will lead to a lot of false detection and every peak-valley will not be captured accurately. A 2nd order IIR filter is sufficient to smooth out the spikes before starting with estimations. Below is a 2nd order IIR transfer function as difference equation:

yi = b1 ∗ xi + b2 ∗ xi−2 − a2 ∗ yi−1 + b3 ∗ xi−1 − a3 ∗ yi−2

where,

yi

: current output

xi−1: previous input

yi−1: previous output

yi−2: output previous to yi−1

xi

: current input

xi−2: input previous to xi−1


Figure 13: 2nd order butterworth IIR filter

Octave’s butter function² was used to get the transfer function coefficients for a low pass configuration. Sampling frequency of 500Hz and a cut-off 3.3Hz (for max HR of 200) was used. Calculated below are the coefficient values:

2https://octave.sourceforge.io/signal/function/butter.html

17 a2 = −1.94137, a3 = 0.94304

b1 = b3 = 4.1762e − 04

b2 = 8.3523e − 04

To visualize filter’s performance, a raw signal was captured from ADC, filter equation was implemented and applied on the input signal in Octave. As seen in Figure 13 filter is quite effective in suppressing noise and produces a smooth output³

### 4.2 Heart Rate

HR is calculated using mountaineer’s method for peak detection (MMPD) in photoplethysmographic signals[4].

In this method, slope is calculated for every sample and as slope changes from positive to negative, sample will corresponding to a peak. Similarly a slope change from negative to positive would be a valley. A count for positive or negative consecutive slopes is also taken and compared with a preset value which updates with every detected peak to improve the robustness of the algorithm. A timer running would store peak timings and time difference between consecutive peaks would correspond to the heart rate. Shown below is a visualization of the algorithm ran on a sample set. Peaks & valleys are captured quite accurately.


Figure 14: HR Algorithm applied to sample data

3Only a 1st order filter was implemented in actual program as it worked ”just fine”, but it is much better to have a 2nd order filter for suitable filtering performance.

18

### 4.3 SpO2 Calculation

As discussed previously in equation (4):

R = Vp2 − Vl2
DC2

/

Vp1 − Vl1
DC1

We don’t want to use signal’s actual peak and valleys for R calculation as that is dependent on heart rate and any averaging of values on top of that would delay the final SpO2% which we intend to obtain. Hence a weight averaging method is used[9], where instantaneous SpO2% is calculated for neighboring samples and averaged together. This ensure multiple instantaneous values are obtained which can be averaged to obtain a final value. Following steps are performed in order:

Figure 15: Selecting samples for instantaneous SpO2

1. Find R between consecutive samples of red and ir signals: Si+1 & Si

R = Si2+1 − Si2
DC2

/

Si1+1 − Si1
DC1

Find SpO2 with this R value which can obtained using a typical relationship curve equation as shown in Figure 4:

SpO2 = −25 ∗ R + 110;

2. Assign a weight to this SpO2 based on the current average. If this instantaneous SpO2 is lower than average, assign a lower weight. If nearer to average, assign a higher weight.
3. Once weights are assigned for 20 samples, calculate a weighted average. Store this weighted average.

19

4. Restart at step 1 and perform 10 such iterations.
5. After 10 iterations, average the calculated weighted averages in each iteration. This becomes the final SpO2. Update this value with the current SpO2 average which is used for assigning weights.

A detailed explanation of this algorithm is in - Pulse Oximetry: Analysis of Theory, Technology and Practise[9]

Finally, an OLED display is refreshed every 5 secs with SpO2% & HR value.

20

### 5 PCB & Enclosure

### 5.1 PCB


Figure 16: Completed PCB


(a) PCB Back | (b) PCB Front

Figure 17: PCB Images

PCB Design was completed on 2 layers with most of the components placed on the back side so that they can be re-flowed easily on a dosa pan. All components on front side are to be hand soldered.

21

- Design also includes a soft latch power on/off switch circuit to easily operate the device.
- A programming header was also added to program the µC via UPDI interface.
- Connection headers were added to connect the leds, battery & photodiode which will be present on bottom compartment of enclosure.
- Header to attach OLED Display.

Sufficient test points were added on front side for easy access to probe and view the signals on oscilloscope.

To keep the PCB size equivalent to that of the OLED display module, 0402 size resistors/capacitors were used.

### 5.2 Enclosure

Enclosure was designed taking reference from a typical Oximeter which has display & PCB on top, a finger insert below and a bottom part with battery compartment.


Figure 18: Completed Enclosure

A reflective setup was implemented with photodiode on top base and pulse leds in bottom compartment.

Securing finger is an important part as any wobble or improper contact would lead to degradation in signal quality and calculated parameters. To achieve a firm pressure onto the finger which would hold it stable in place, a safety pin was used (removing the clip part) in the rotation mechanism.

22


(a) Photodiode compartment | (b) Spacers for pcb

Figure 19: Top Base


(a) Battery compartment | (b) Led compartment

Figure 20: Bottom Base

In idle position, pin would be in natural non-extended state hence both base parts would be closed. When a finger is inserted, lid needs

23

(a) Safety pin | (b) Side view of pin

Figure 21: Pin mounted in bottom base

to go up via the rotational mechanism as that is the only path to accommodate the finger. This would cause the upper part connected with pin to push down on finger which would lead to a firm grip to form ensuring good contact with photodiode and led.


Figure 22: Snap fit cross-section

Snap fit elements were implemented making it easier to fit and remove the cover parts whenever required.

24

### 6 References

[1] Hartmann Vera, Liu Haipeng. Quantitative Comparison of Photoplethysmographic Waveform Characteristics: Effect of Measurement Site Frontiers in Physiology , vol 10 (2019) https://www.frontiersin.org/article/10.3389/fphys.2019.00198
[2] Ash, Caerwyn et al. Effect of wavelength and beam width on penetration in light-tissue interaction using computational methods. Lasers in medical science vol. 32,8 (2017): 1909-1918. https: //www.ncbi.nlm.nih.gov/pmc/articles/PMC5653719/
[3] Feiner, John R. MD, Severinghaus. Dark Skin Decreases the Accuracy of Pulse Oximeters at Low Oxygen Saturation December 2007 - Volume 105 - Issue 6 - p S18-S23 https://journals.lww.com/anesthesia-analgesia/Fulltext/2007/12001/Dark_Skin_Decreases_the_Accuracy_of_Pulse.4.aspx (https://journals.lww.com/anesthesia-analgesia/Fulltext/2007/12001/Dark_Skin_Decreases_the_Accuracy_of_Pulse.4.aspx)
[4] ArgÃĳello-Prada, Erick Javier. The mountaineer’s method for peak detection in photoplethysmographic signals. Revista Facultad De Ingenieria-universidad De Antioquia 2018 (2019): 42-50 https://api.semanticscholar.org/CorpusID:116767900
[5] Santiago Lopez, Freescale Semiconductor. Pulse Oxime-
ter | Fundamentals | and | Design | Document | Number:
AN4327, | Rev. 2, | 11/2012 https://www.nxp.com/docs/
en/application-note/AN4327.pdf (https://www.nxp.com/docs/en/application-note/AN4327.pdf)
[6] Praveen Aroul, Texas Instruments. Miniaturized Pulse Oximeter Reference Design UserâĂŹs Guide and Test Report TIDA-00311 https://www.ti.com/lit/pdf/tidu542
[7] Zhang Feng, Microchip Technology Inc. Pulse Oximeter Design Using MicrochipâĂŹs Analog Devices and dsPICÂő Digital Signal Controllers (DSCs) AN1525, 04/28/2015 http://ww1.microchip.com/downloads/en/Appnotes/00001525B.pdf (http://ww1.microchip.com/downloads/en/Appnotes/00001525B.pdf)
[8] Dr. Neil Townsend, Department of Engineering Science, University of Oxford. C3B Medical Electronics Lecture Notes https://www.robots.ox.ac.uk/˜neil/teaching/lectures/med_elec/notes6.pdf (https://www.robots.ox.ac.uk/~neil/teaching/lectures/med_elec/notes6.pdf)
[9] Michael W. Wukitsch, BA,Michael T. Petterson. Pulse Oximetry: Analysis of Theory,Technology and Practice https://doi.org/10.1007/BF01617328 (https://doi.org/10.1007/BF01617328)

25

### 7 Closing Comments

I referred the listed documents extensively throughout the process specifically [5], [6], [7], [8], [9] to close gaps in my understanding and to improve/revisit the design.

Completing this project taught me lot of things from a design perspective and a lot of respect for the products that I use on daily basis considering the amount of iterations something must have went through and enormous number of checks/edge cases to ensure it works just right.

For me, this project took close to 7 months for completion, considering I worked 20hrs/week on average. I made 3 iterations in total during this timeline, documented is the 3rd version. There are still a lot of improvements i can think of hence a shortcomings/recommended improvements page is added to project directory where i have listed all further improvements or current issues which can be worked on. I wouldn’t want to progress these anymore as somewhere i feel the initial goal with which i started off has met:

- Making something from scratch(at least a suitable prototype) and documenting the entire project in 2 different languages.
- A YouTube Vlog of the project.

I hadn’t done any of this in the past hence this project required me to change myself to accomplish it. Most important lessons that i have learned from this journey are:

- Never let something which appears difficult or out of reach contemplate your decision to work on it. You know nothing so everything is going to be difficult to understand but it shouldn’t become a filter for choosing what to work on.
- Consistency. There were many issues with design that I found on weekends which later got resolved in the next weekend only because there was consistency and I was involved with the problem on a daily basis performing new workarounds every day.

I would end this document now. If you have any suggestions or comments, you can reach me out on Twitter @yskabhijeet. (https://twitter.com/yskabhijeet)

26

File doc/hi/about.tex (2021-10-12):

भारत में COVID-19 की लहर के दौरान, मैंने देखा, बहुत लोग घर पर ऑक्सीजन के स्तर की निगरानी के लिए मेडिकल स्टोर और ऑनलाइन ऑक्सीमीटर खरीद रहें थे। मैं काफ़ी उत्सुक था, यह जानने के लिये कि उंगली से जुड़ा यह छोटा उपकरण हृदय गति और ऑक्सीजन संतृप्ति की गणना कैसे कर सक़ता है? इस सवाल ने मुझे शोध करने और समझने को प्रेरित किया कि वास्तव में ऑक्सीमीटर कैसे काम करता है और क्या मैं इसे खुद पुरा बना सक़ता हूं। इस प्रक्रिया में मुझे एहसास हुआ, सभी विवरणों को एक समझ दस्तावेज़ में लिखना सही होगा जो मेरे लिए एक स्मृति के रूप में काम करेगा और दूसरों के लिए भी मददगार हो सक़ता है।
साथ ही, मैं \LaTeX \hspace{1pt} सीखना शुरू करना चाहता था ताकि भविष्य की सभी परियोजनाओं के लिए सुंदर लिखित दस्तावेज़ तैयार किये जा सके।\bigskip

इस लेखन मे, ऑक्सीमीटर क्या है, ऑक्सीजन संतृप्ति और हृदय गति प्राप्त करने के लिए इलेक्ट्रॉनिक सर्किट का उपयोग कैसे किया जा सक़ता है, इसका एक संक्षिप्त सिद्धांत प्रस्तुत करने का प्रयास किया गया है। आवश्यक सर्किट तत्वों और ऐल्गोरिद्म पर भी चर्चा की गई है। यह माना गया है कि पाठक को निम्नलिखित विषयों का ज्ञान हैै:

\begin{itemize}
	\item बुनियादी सर्किट विश्लेषण \& इलेक्ट्रॉनिक तत्व
	\item ऑप एंप \& ट्रांजिस्टर के नियम
\end{itemize}

\bigskip

मैं इलेक्ट्रॉनिक्स सीखने कि यात्रा में नौसिखिया हूं, इसलिए इस लेख में गलतियां हो सकती हैं। प्रस्तुत जानकारी की सत्यता की जांच मेरे अलावा किसी अन्य व्यक्ति ने नहीं की है।
यह लेख इसलिए लिखा गया था ताकि ज्ञान का स्रोत बन सके कि ऑक्सीमीटर कैसे बनाया जाता है या ऑक्सीमीटर कैसे काम करता है। प्रस्तुत डिज़ाइन का उपयोग किसी भी जीवन समर्थन प्रणाली में नहीं किया जाना है।

\bigskip
यह दस्तावेज़ TexStudio editor मे लिखा गया है।	

सभी चित्र Inkscape से तैयार किए गए है।

लेखाचित्र GNU Octave मे बनाये गये है।

PCB \& Schematics को Kicad मे डिज़ाइन किया गया है।

एन्क्लोज़र FreeCAD मे डिज़ाइन किया गया है।

\medskip
परियोजना से संबंधित सभी फाइलें यहां है: \url{https://github.com/yskab/dhadak}

वीडियो श्रंखला: \url{https://youtu.be/QoOAn5z_qHc}

\medskip
यदि कोई गलतियां मिलती है या सुधार करना चाहते हैं तो कृपया Github पर संपर्क करें। 

\medskip
पोस्ट और संदेशों के लिए Twitter पर मुझ तक पहुंच सकते हैं 
\href{https://twitter.com/yskabhijeet}{@yskabhijeet}

\par

\vfill
\hfill
{\Large\bfseries वाई एस के अभिजीत}\par
\hfill
\large \today

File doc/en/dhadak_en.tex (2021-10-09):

\documentclass[10pt,a4paper]{article}

\usepackage{tikz}
\usetikzlibrary{positioning, arrows, shapes.geometric}
\usepackage{graphicx}
\usepackage{caption, copyrightbox}
\usepackage{amsmath}
\usepackage{circuitikz}
\usepackage{subfig}
\usepackage{siunitx}
\usepackage{xfrac}
\usepackage[parfill]{parskip}
\usepackage{xcolor}
\usepackage[nottoc,numbib]{tocbibind}
\usepackage{lmodern}

\usepackage[hidelinks]{hyperref}
\hypersetup{
	pdftitle={Dhadak - A Pulse Oximeter},
	pdfsubject={Engineering, Circuit Design, Medical},
	pdfauthor={Y S K Abhijeet},
	pdfkeywords={oximeter, circuit design, electronics, heart rate}
}

\usepackage{pgfplots}
\pgfplotsset{compat=1.15}

\begin{document}
			
	\pagenumbering{roman}		
	\begin{titlepage}
		\vspace*{5cm}
		{\centering
			
			\par
		}
		\vspace{4cm}
		\hfil \Large\bfseries English \hfil
		\vfill
	\end{titlepage}

	\include{about}
	\tableofcontents
	\pagebreak
	\pagenumbering{arabic}
	
	\include{intro}	
	\include{comp}
	\include{circuit}
	\include{algo}
	\include{enc}
	
	\pagebreak

	\begin{thebibliography}{10}		

		\bibitem{light}
		Hartmann Vera, Liu Haipeng.
		\textit{Quantitative Comparison of Photoplethysmographic 
		Waveform Characteristics: Effect of Measurement Site}
		Frontiers in Physiology , vol 10 (2019)
		\url{https://www.frontiersin.org/article/10.3389/fphys.2019.00198}

		\bibitem{penetrate}
		Ash, Caerwyn et al.
		\textit{Effect of wavelength and beam width on 
		penetration in light-tissue interaction using computational methods.}
		Lasers in medical science vol. 32,8 (2017): 1909-1918.
		\url{https://www.ncbi.nlm.nih.gov/pmc/articles/PMC5653719/}		
		
		\bibitem{skin}
		Feiner, John R. MD, Severinghaus.
		\textit{Dark Skin Decreases the Accuracy of Pulse Oximeters at 
		Low Oxygen Saturation}
		December 2007 - Volume 105 - Issue 6 - p S18-S23
		\url{https://journals.lww.com/anesthesia-analgesia/Fulltext/2007/12001/Dark_Skin_Decreases_the_Accuracy_of_Pulse.4.aspx}		
		
		\bibitem{mmpd} 
		Argüello-Prada, Erick Javier. 
		\textit{The mountaineer's method for peak detection in photoplethysmographic signals.} 
		Revista Facultad De Ingenieria-universidad De Antioquia 2018 (2019): 42-50
		\url{https://api.semanticscholar.org/CorpusID:116767900}
		 
		\bibitem{nxp} 
		Santiago Lopez, Freescale Semiconductor.
		\textit{Pulse Oximeter Fundamentals and Design} 
		Document Number: AN4327, Rev. 2, 11/2012
		\url{https://www.nxp.com/docs/en/application-note/AN4327.pdf}
		
		\bibitem{ti}
		Praveen Aroul, Texas Instruments.
		\textit{Miniaturized Pulse Oximeter Reference Design}
		User’s Guide and Test Report TIDA-00311
		\url{https://www.ti.com/lit/pdf/tidu542}
		
		\bibitem{micro}
		Zhang Feng, Microchip Technology Inc.
		\textit{Pulse Oximeter Design Using Microchip’s Analog Devices
		and dsPIC® Digital Signal Controllers (DSCs)}
		AN1525,   04/28/2015
		\url{http://ww1.microchip.com/downloads/en/Appnotes/00001525B.pdf}

		\bibitem{oxf}
		Dr. Neil Townsend, Department of Engineering Science, University of Oxford.
		\textit{C3B Medical Electronics Lecture Notes}
		\url{https://www.robots.ox.ac.uk/~neil/teaching/lectures/med_elec/notes6.pdf}	

		\bibitem{wuk}
		Michael W. Wukitsch, BA,Michael T. Petterson.
		\textit{Pulse Oximetry: Analysis of Theory,Technology and Practice}
		\url{https://doi.org/10.1007/BF01617328}	
	\end{thebibliography}

	\pagebreak
	\section{Closing Comments}
	
	I referred the listed documents extensively throughout the process specifically \cite{nxp}, \cite{ti}, \cite{micro}, \cite{oxf}, \cite{wuk} to close gaps in my understanding and to improve/revisit the design.\par
	\bigskip
	Completing this project taught me lot of things from a design perspective and a lot of respect for the products that I use on daily basis considering the amount of iterations something must have went through and enormous number of checks/edge cases to ensure it works just right.
	
	For me, this project took close to 7 months for completion, considering I worked 20hrs/week on average. I made 3 iterations in total during this timeline, documented is the 3\textsuperscript{rd} version. There are still a lot of improvements i can think of hence a shortcomings/recommended improvements page is added to project directory where i have listed all further improvements or current issues which can be worked on. I wouldn't want to progress these anymore as somewhere i feel the initial goal with which i started off has met:
	
	\begin{itemize}
		\item Making something from scratch(at least a suitable prototype) and documenting the entire project in 2 different languages.
		\item A YouTube Vlog of the project.
	\end{itemize}

	I hadn't done any of this in the past hence this project required me to change myself to accomplish it. Most important lessons that i have learned from this journey are:
	
	\begin{itemize}
	\item Never let something which appears difficult or out of reach contemplate your decision to work on it. You know nothing so everything is going to be difficult to understand but it shouldn't become a filter for choosing what to work on.
	
	\item Consistency. There were many issues with design that I found on weekends which later got resolved in the next weekend only because there was consistency and I was involved with the problem on a daily basis performing new workarounds every day.
	\end{itemize}

	\bigskip
	I would end this document now. If you have any suggestions or comments, you can reach me out on Twitter
	\href{https://twitter.com/yskabhijeet}{@yskabhijeet}.

\end{document}

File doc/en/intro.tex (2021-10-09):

	
\section{Introduction}

	Oximetry is the process of measuring the concentration of oxygen in blood (oxygen saturation - SpO\textsubscript{2}). Normal levels of SpO\textsubscript{2} should usually be around 95\% to 100\%, level below 90\% could lead to Hypoxemia which can cause shortness of breath and headache\footnote{\url{https://www.mayoclinic.org/symptoms/hypoxemia/basics/definition/sym-20050930}}.

\subsection{Cardiac Cycle}

	Red blood cells contain Hemoglobin, a protein which when comes in contact with fresh oxygen via lungs forms Oxygenated Hemoglobin (HbO\textsubscript{2}). This Oxygenated blood is carried from the lungs to left side of the heart, which pumps this blood around the body through arteries. The cells of the body convert the chemical energy from oxygen molecules in red blood cells into Adenosine Triphosphate (ATP). ATP is stored in the cell and can be used for organism's life support system as required. Absence of oxygen in red blood cells due to conversion into ATP forms Deoxygenated Hemoglobin (Hb).\medskip

	This deoxygenated blood returns through the veins to right side of the heart, from there the blood is pumped into lungs to expel carbon dioxide and again fresh oxygen is inhaled and blood gets oxygenated. This completes a single Cardiac Cycle.

\subsection{Oximetry Principle}

	Pulse Oximeter is based on PPG (Photoplethysmography) wherein a light source is projected and a detector is used to measure volumetric changes in blood. It has been observed that Hb has a higher absorption when red wavelength is passed through while HbO\textsubscript{2} has a higher absorption towards infrared wavelength source (Figure \ref{fig:spectrum}). If we can relate the detected output with concentration of Hb/HbO\textsubscript{2} in blood, a relation can be obtained to calculate SpO\textsubscript{2}.

	\begin{figure}[ht!]
		\centering
		
		\caption{Absorption Spectra - Hb/HbO\textsubscript{2}}
		\label{fig:spectrum}
	\end{figure}

	\begin{figure}[ht!]
		\centering
		
		\caption{PPG waveform when a single light source is projected}
		\label{fig:ppg}
	\end{figure}

	Heart pumps blood with each cardiac cycle and this leads to change in blood volume in the artery. When light is passed through (finger, earlobe, wrist\cite{light} depending on it's wavelength, Hb/HbO\textsubscript{2} components will also get absorbed and PPG signal is obtained as an output. Signal peaks correspond to completion of a cardiac cycle (heart beat). This varying signal also has a DC level due to absorption of light source by skin, venous blood and tissue.

	From this understanding, if we can find molecular concentrations of Hb and HbO\textsubscript{2} in a defined blood volume, SpO\textsubscript{2} can be calculated as a ratio of oxygenated blood concentration to total concentration: 

	\begin{equation}
		SpO\textsubscript{2} = \frac{HbO\textsubscript{2}}{Hb + 	HbO\textsubscript{2}}
	\end{equation}
	
	According to Beer-Lambert law:
	
	\begin{equation}		
		\log_{10}\frac{I}{I_o} = \epsilon l c
	\end{equation}	
	
	$I -$ Transmitted light intensity
	
	$I\textsubscript{o}-$ Incident light intensity
	
	$l -$ length
	
	$c -$ Molecular concentration
	
	$\epsilon -$ Molar absorption coefficient

	\begin{figure}[ht!]
		\centering
		
		\caption{Light source projected onto a finger}
		\label{fig:finger}
	\end{figure}
	
	As seen in Figure \ref{fig:finger}, a light source is projected onto a finger and transmitted light is detected on the other end. Infrared and Red light is pulsed individually. For infrared source:
	
	\[	
	c_1 = 	\frac{\log_{10}\frac{I_1}{I_{o1}}}{\epsilon_1 l}
	\]	
	
	Since HbO\textsubscript{2} has higher absorption for infrared wavelength,

	\[	
	HbO_2 = \frac{\log_{10}\frac{I_1}{I_{o1}}}{\epsilon_1 	l}
	\]	
	
	Similarly for red,
	\[	
	Hb = \frac{\log_{10}\frac{I_2}{I_{o2}}}{\epsilon_2 	l}
	\]
	
	According to (1),

	\[	
	SpO_2 =  \frac{\frac{\log_{10}\frac{I_1}{I_{o1}}}{\epsilon_1 l}}		
	{\frac{\log_{10}\frac{I_2}{I_{o2}}}{\epsilon_2 l} + 	\frac{\log_{10}\frac{I_1}{I{o1}}}{\epsilon_1 l}}
	\]	
	
	if $R = \frac{\log_{10}\frac{I_2}{I_{o2}}}{\log_{10}\frac{I_1}{I_{o1}}}$,
	
	\[	
	SpO_2 = \frac{\frac{1}{\epsilon_1}}{\frac{R}{\epsilon_2} + \frac{1}{\epsilon_1}}
	\]	
	
	\begin{equation}
		SpO_2 = \frac{\epsilon_2}{R\epsilon_1 + \epsilon_2}
	\end{equation}	

	SpO\textsubscript{2} mostly depends on R, we can consider calculating R and later comparing with a calibrated reference to get the actual SpO\textsubscript{2}.
	
	Since Incident light intensity level would be constant while pulsed, R would depend only upon I\textsubscript{1} and I\textsubscript{2},

	\[
	R \approx \frac{\log_{10}{I_2}}{\log_{10}{I_1}} \approx \frac{I_2}{I_1} \approx \frac{AC_2}{AC_1}
	\]		
	
	We need not calculate the logarithm, as the actual SpO\textsubscript{2} would be obtained from a Look up table or an empirical equation which demonstrates relation of R to SpO\textsubscript{2}. Standard oximeter manufacturers would test their device on large group of subjects and obtain the R values and subject's actual SpO\textsubscript{2} using a separate calibrated meter to prepare a relationship curve. Once this mapping is obtained, SpO\textsubscript{2} for any subject can be calculated using the relationship.
	
	\begin{figure}[ht!]
	\centering	
	\begin{tikzpicture}
		\begin{axis}[
			xlabel = R,
			ylabel = SpO\textsubscript{2}\%]
			\addplot coordinates {
				(0.4, 100)
				(1, 85)
				(1.5, 72.5)
				(2, 60)
				(2.5, 47.5)
				(3, 35)
				(3.5, 22.5)
				(4, 10)
				(4.4,0)
			};
			
		\end{axis}
	\end{tikzpicture}
	\caption{A typical relationship curve R vs SpO\textsubscript{2}}
	\label{fig:curve}
	\end{figure}

	Since detected IR and Red signals can have varying DC levels, we need to normalize the ratio first by dividing the DC levels so that a direct comparison of the PPG (AC component) can be performed as that caries the absorbed/un-absorbed information, hence R now becomes:

	\[
		R = \sfrac{\frac{AC_2}{DC_2}}{{\frac{AC_1}{DC_1}}}
	\]	
	
	\begin{figure}[ht!]
		\centering
		\subfloat[Before Normalization
		]{}
		\hfill
		\subfloat[After Normalization
		]{}
		\caption{Effect of Normalization}
		\label{fig:ppgnorm}
	\end{figure}

	\begin{equation}
	\label{eq:calc}	
	R = \sfrac{\frac{V_{p2} - V_{l2}}{DC_2}}{\frac{V_{p1} - V_{l1}}{DC_1}}
	\end{equation}	 

	As shown in Figure \ref{fig:ppgnorm},
	
	$V_{p1} - $  Ir Peak
	
	$V_{l1} - $  Ir Valley
	
	$V_{p2} - $  Red Peak
	
	$V_{l2} - $  Red Valley
	
	$DC_1 - $  Ir DC level
	
	$DC_2 - $  Red DC level

	This value of R when compared with relationship curve would give the actual SpO\textsubscript{2}.
	
	We can consider calculating R for a set of samples and average them, instead of
	waiting for peaks and valleys to arrive. In this implementation, R is calculated between neighboring samples and a weighted average{\cite{wuk}} is calculated for final value. This is discussed further in SpO\textsubscript{2} calculation algorithm section.

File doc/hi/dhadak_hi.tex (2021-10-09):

% !TeX program = xelatex
\documentclass[10pt,a4paper]{article}

\usepackage{polyglossia}
\setdefaultlanguage{hindi}
\newfontfamily\devanagarifont[Script=Devanagari]{Eczar}
\setotherlanguages{english}

\usepackage{tikz}
\usetikzlibrary{positioning, arrows, shapes.geometric}
\usepackage{graphicx}
\usepackage{caption, copyrightbox}
\usepackage{amsmath}
\usepackage{circuitikz}
\usepackage{subfig}
\usepackage{siunitx}
\usepackage{xfrac}
\usepackage[parfill]{parskip}
\usepackage{xcolor}
\usepackage[nottoc,numbib]{tocbibind}
\usepackage{lmodern}

\usepackage[hidelinks]{hyperref}
\hypersetup{
	pdftitle={Dhadak - A Pulse Oximeter},
	pdfsubject={Engineering, Circuit Design, Medical},
	pdfauthor={Y S K Abhijeet},
	pdfkeywords={oximeter, circuit design, electronics, heart rate}
}

\usepackage{pgfplots}
\pgfplotsset{compat=1.15}
\renewcommand\UrlFont{\ttfamilylatin}

\begin{document}
	
	\pagenumbering{roman}
	\begin{titlepage}
		\vspace*{5cm}
		{\centering
			
			\par
		}
		\vspace{4cm}
		\hfil \Large\bfseries हिन्दी \hfil
		\vfill
	\end{titlepage}
	
	\include{about}
	\tableofcontents
	\pagebreak
	\pagenumbering{arabic}
	
	\include{intro}	
	\include{comp}
	\include{circuit}
	\include{algo}
	\include{enc}
	\pagebreak

	\begin{thebibliography}{10}		
		\begin{english}
			
		\bibitem{light}
		Hartmann Vera, Liu Haipeng.
		\textit{Quantitative Comparison of Photoplethysmographic 
			Waveform Characteristics: Effect of Measurement Site}
		Frontiers in Physiology , vol 10 (2019)
		\url{https://www.frontiersin.org/article/10.3389/fphys.2019.00198}
		
		\bibitem{penetrate}
		Ash, Caerwyn et al.
		\textit{Effect of wavelength and beam width on 
			penetration in light-tissue interaction using computational methods.}
		Lasers in medical science vol. 32,8 (2017): 1909-1918.
		\url{https://www.ncbi.nlm.nih.gov/pmc/articles/PMC5653719/}		
		
		\bibitem{skin}
		Feiner, John R. MD, Severinghaus.
		\textit{Dark Skin Decreases the Accuracy of Pulse Oximeters at 
			Low Oxygen Saturation}
		December 2007 - Volume 105 - Issue 6 - p S18-S23
		\url{https://journals.lww.com/anesthesia-analgesia/Fulltext/2007/12001/Dark_Skin_Decreases_the_Accuracy_of_Pulse.4.aspx}		
		
		\bibitem{mmpd} 
		Argüello-Prada, Erick Javier. 
		\textit{The mountaineer's method for peak detection in photoplethysmographic signals.} 
		Revista Facultad De Ingenieria-universidad De Antioquia 2018 (2019): 42-50
		\url{https://api.semanticscholar.org/CorpusID:116767900}
		
		\bibitem{nxp} 
		Santiago Lopez, Freescale Semiconductor.
		\textit{Pulse Oximeter Fundamentals and Design} 
		Document Number: AN4327, Rev. 2, 11/2012
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

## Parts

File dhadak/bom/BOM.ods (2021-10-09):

Source: | /home/abhijeet/Desktop/dhadak/dhadak_PCB_v2/dhadak/dhadak.sch
Date: | Sat Aug 7 22:58:52 2021
Tool: | Eeschema 5.1.10-88a1d61d58~88~ubuntu18.04.1
Generator: | /usr/share/kicad/plugins/bom_csv_grouped_by_value.py
Component Count: | 76
Collated Components:
Item | Qty | Reference(s) | Value | LibPart | Footprint
1 | 7 | C1, C2, C3, C4, C5, C7, C10 | 0.1u | Device:C | Capacitor_SMD:C_0402_1005Metric
2 | 2 | C6, C8 | 10u | Device:C | Capacitor_SMD:C_0805_2012Metric
3 | 1 | C9 | 100p | Device:C | Capacitor_SMD:C_0805_2012Metric
4 | 1 | IC1 | MCP47FEB02A0-E_ST | mcp47:MCP47FEB02A0-E_ST | Package_SO:TSSOP-8_4.4x3mm_P0.65mm
5 | 1 | J1 | OLED_PORT | Connector_Generic:Conn_01x04 | Connector_PinHeader_2.54mm:PinHeader_1x04_P2.54mm_Vertical
6 | 1 | J2 | PROG_PORT | Connector_Generic:Conn_01x04 | Connector_PinHeader_2.54mm:PinHeader_1x04_P2.54mm_Vertical
7 | 1 | J3 | PD_PORT | Connector_Generic:Conn_01x02 | Connector_PinHeader_2.00mm:PinHeader_1x02_P2.00mm_Vertical
8 | 1 | J4 | EXT_PORT | Connector_Generic:Conn_01x05 | Connector_PinHeader_2.54mm:PinHeader_1x05_P2.54mm_Vertical
9 | 13 | Q1, Q2, Q3, Q5, Q6, Q9, Q10, Q11, Q12, Q13, Q14, Q15, Q16 | BC847 | Device:Q_NPN_BEC | Package_TO_SOT_SMD:SOT-23
10 | 1 | Q4 | SI2305 | Device:Q_PMOS_GSD | Package_TO_SOT_SMD:SOT-23
11 | 2 | Q7, Q8 | BC857 | Device:Q_PNP_BEC | Package_TO_SOT_SMD:SOT-23
12 | 20 | R3, R5, R14, R15, R17, R18, R25, R26, R29, R30, R35, R36, R37, R38, R39, R40, R41, R42, R43, R44 | 4.7K | Device:R_US | Resistor_SMD:R_0402_1005Metric
13 | 13 | R4, R8, R13, R21, R22, R23, R24, R27, R28, R31, R32, R33, R34 | 10K | Device:R_US | Resistor_SMD:R_0402_1005Metric
14 | 1 | R6 | 20 | Device:R_US | Resistor_SMD:R_0805_2012Metric
15 | 1 | R7 | 330 | Device:R_US | Resistor_SMD:R_0402_1005Metric
16 | 5 | R9, R10, R11, R19, R20 | 100K | Device:R_US | Resistor_SMD:R_0402_1005Metric
17 | 2 | R12, R16 | 200K | Device:R_US | Resistor_SMD:R_0402_1005Metric
18 | 1 | SW1 | SW_PWR | Switch:SW_SPST | Button_Switch_THT:SW_PUSH_6mm
19 | 1 | U1 | ATmega4808-A | MCU_Microchip_ATmega:ATmega4808-A | Package_QFP:TQFP-32_7x7mm_P0.8mm
20 | 1 | U2 | LMV324 | Amplifier_Operational:LMV324 | Package_SO:TSSOP-14_4.4x5mm_P0.65mm

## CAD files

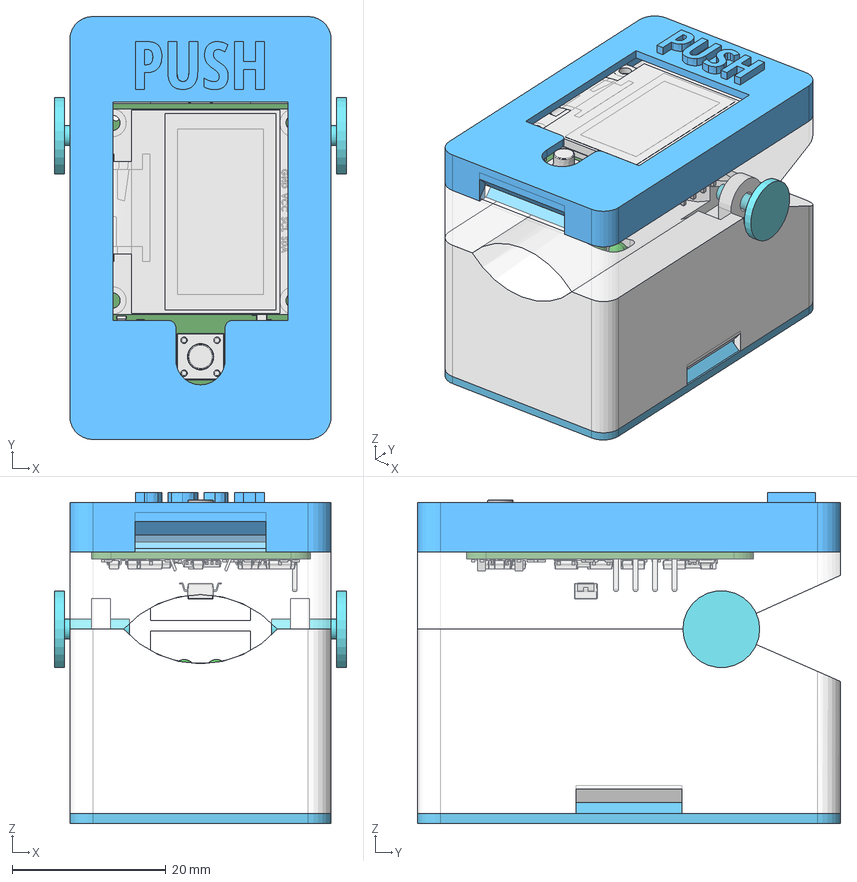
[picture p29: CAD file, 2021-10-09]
enclosure/enc.FCStd
38.0 x 55.0 x 43.1 mm
top_base
bot_base
AAA1
AAA2
keystone_5213
keystone2_5213
led_energy
led_energy002
top_cover
bot_cover
pivot
QSB34CGR
pivot001

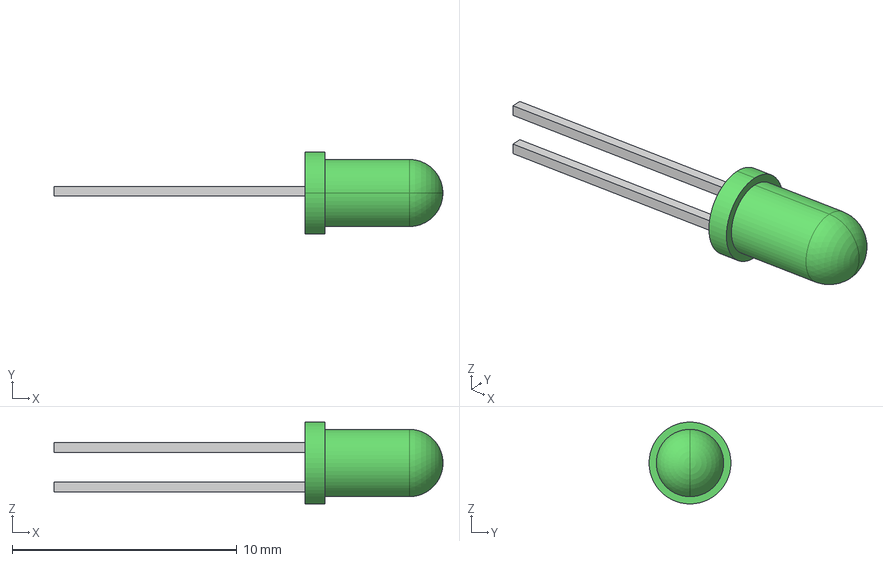
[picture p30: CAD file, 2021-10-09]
enclosure/External Models/3mm_LED.stp
17.3 x 3.64 x 3.64 mm
led_energy
led_pin.1.1.1
led_pin.2.1

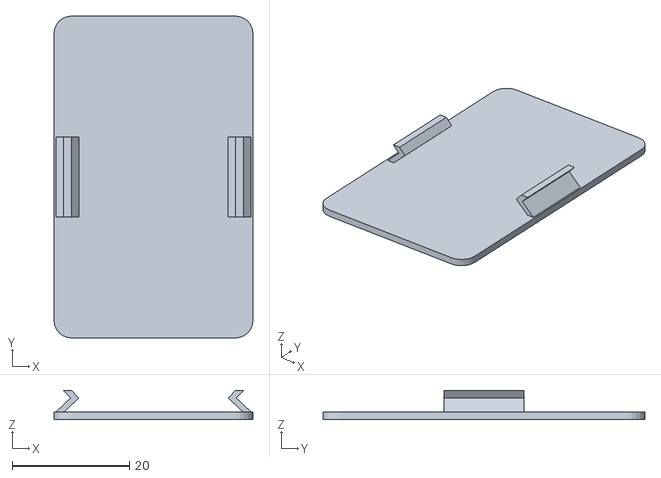
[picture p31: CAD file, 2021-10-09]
enclosure/STLs/bot_cover.stl
34.0 x 55.0 x 5.00

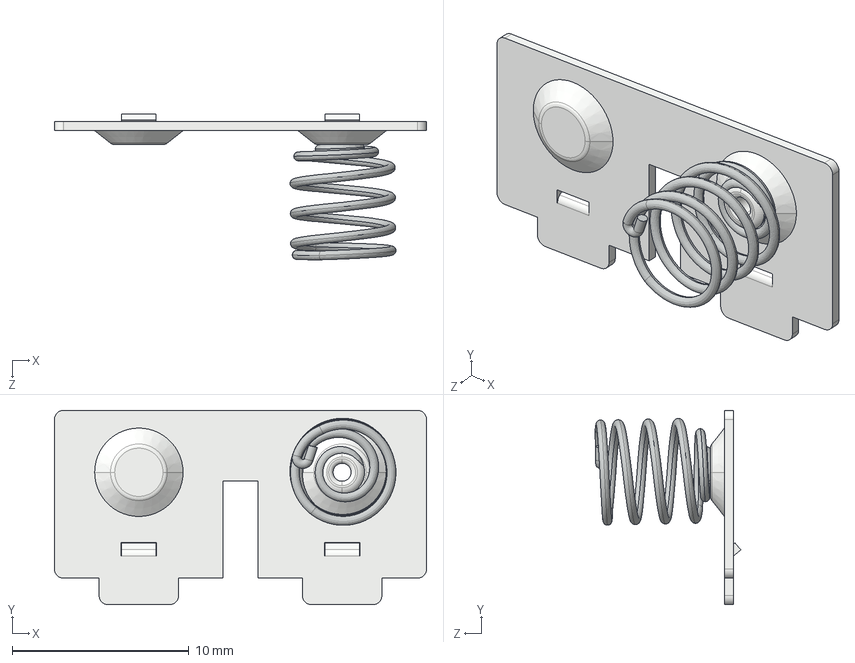
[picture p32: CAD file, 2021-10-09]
enclosure/External Models/keystone-PN5214.STEP
21.1 x 11.0 x 8.25 mm

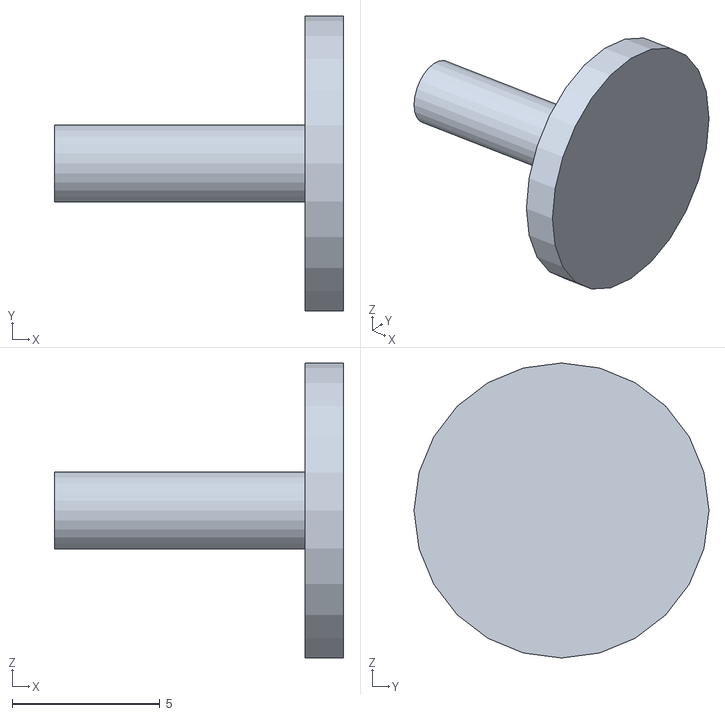
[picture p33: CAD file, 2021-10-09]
enclosure/STLs/pivot.stl
9.80 x 10.0 x 10.0

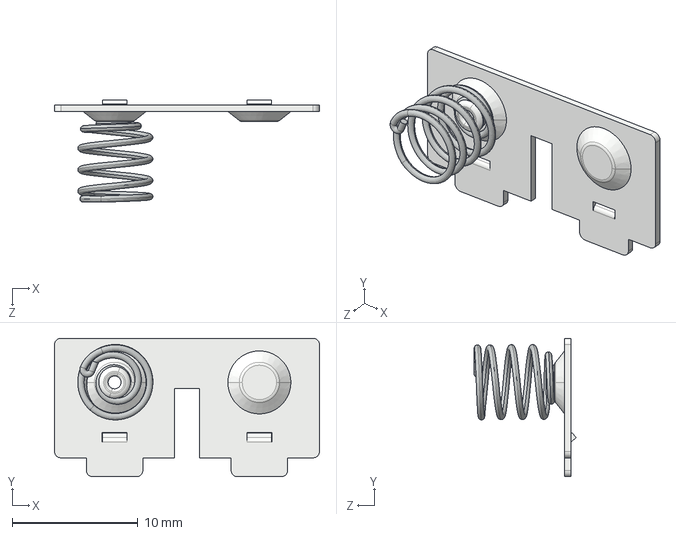
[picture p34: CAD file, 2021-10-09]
enclosure/External Models/keystone-PN5213.STEP
21.1 x 11.0 x 8.14 mm

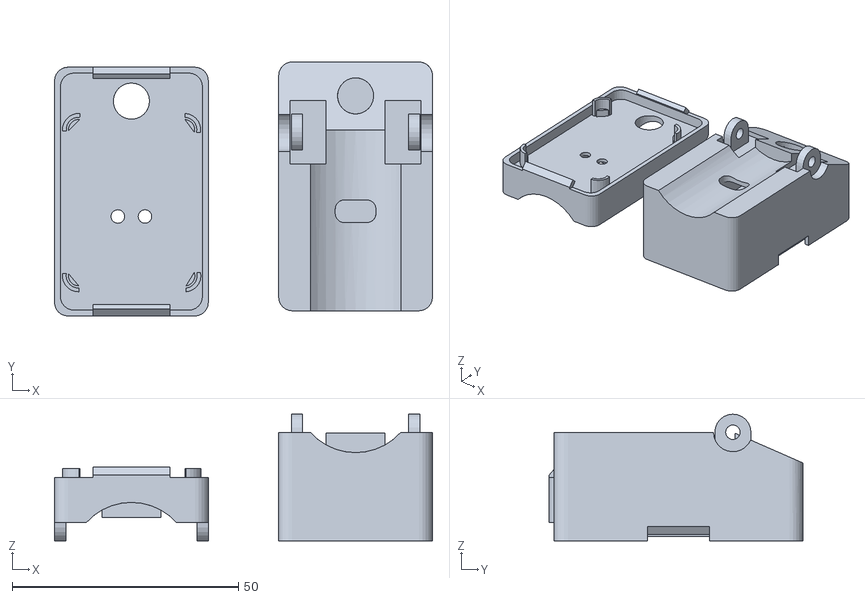
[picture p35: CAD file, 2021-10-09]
enclosure/STLs/model_base.stl
83.5 x 56.2 x 28.0

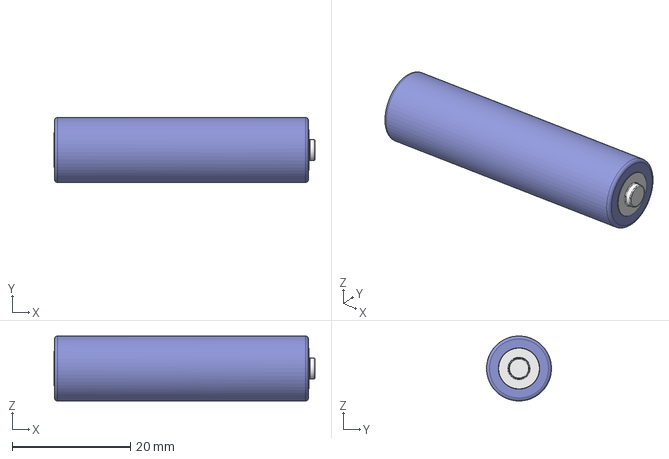
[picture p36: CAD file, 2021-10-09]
enclosure/External Models/AAA Batterie.step
44.2 x 11.0 x 11.0 mm

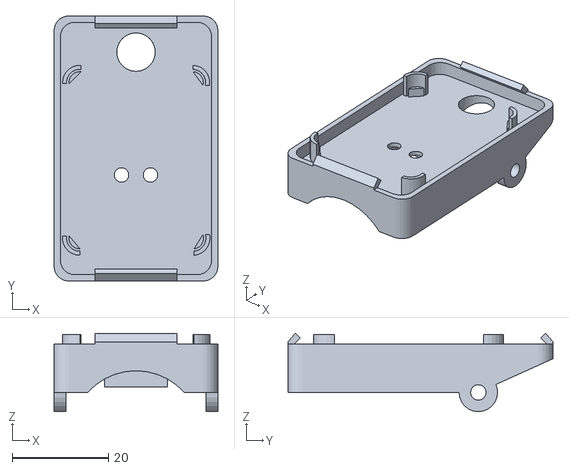
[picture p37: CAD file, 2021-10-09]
enclosure/STLs/top_base.stl
34.0 x 55.0 x 16.3

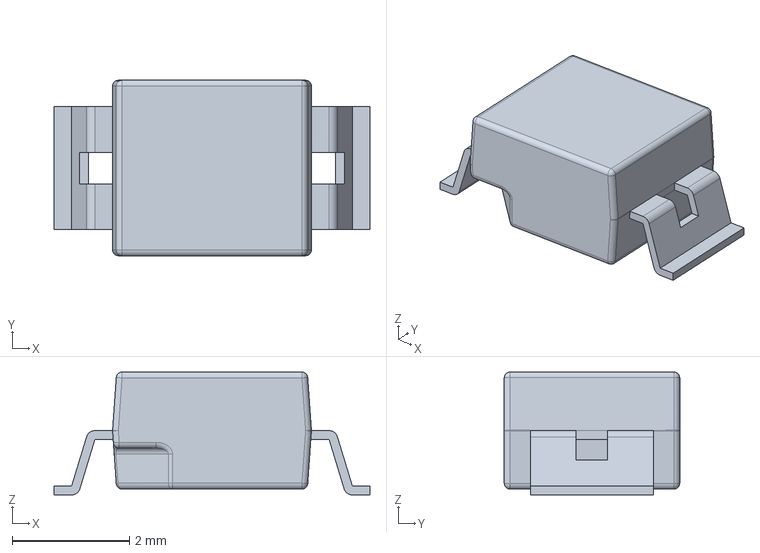
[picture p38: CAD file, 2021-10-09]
enclosure/External Models/Fairchild_-_QSB34CGR.step
5.40 x 3.00 x 2.10 mm

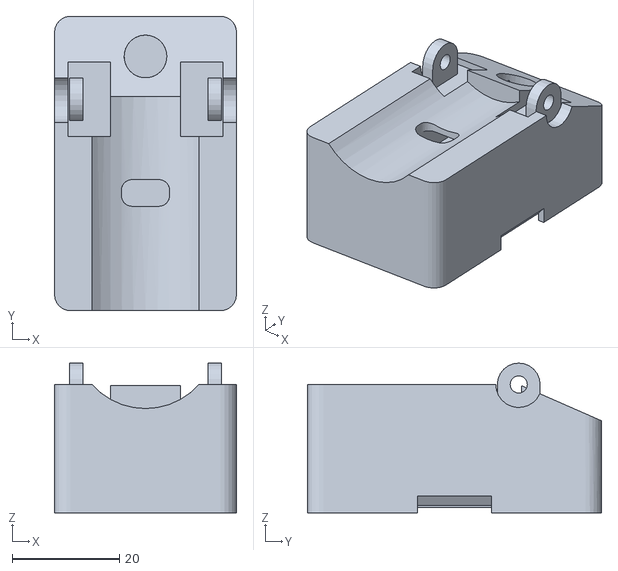
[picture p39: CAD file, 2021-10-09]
enclosure/STLs/bot_base.stl
34.0 x 55.0 x 28.0

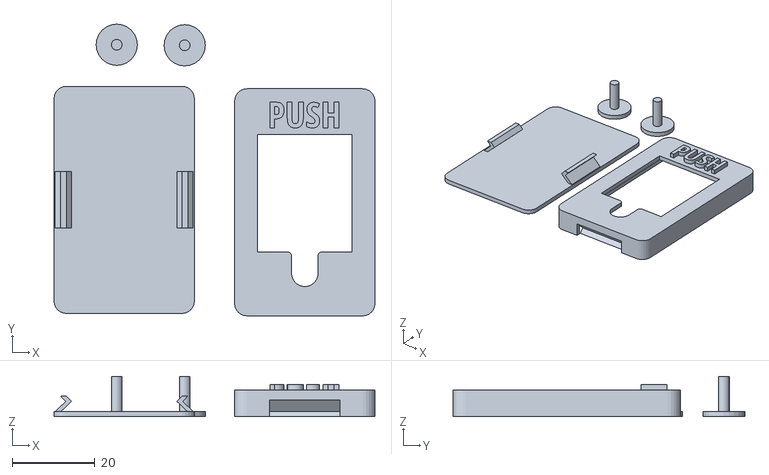
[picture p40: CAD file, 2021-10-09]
enclosure/STLs/model_cover.stl
77.7 x 70.7 x 9.80

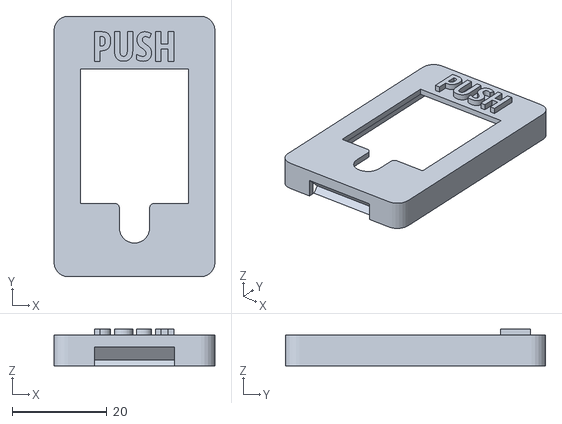
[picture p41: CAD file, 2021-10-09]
enclosure/STLs/top_cover.stl
34.0 x 55.0 x 7.80

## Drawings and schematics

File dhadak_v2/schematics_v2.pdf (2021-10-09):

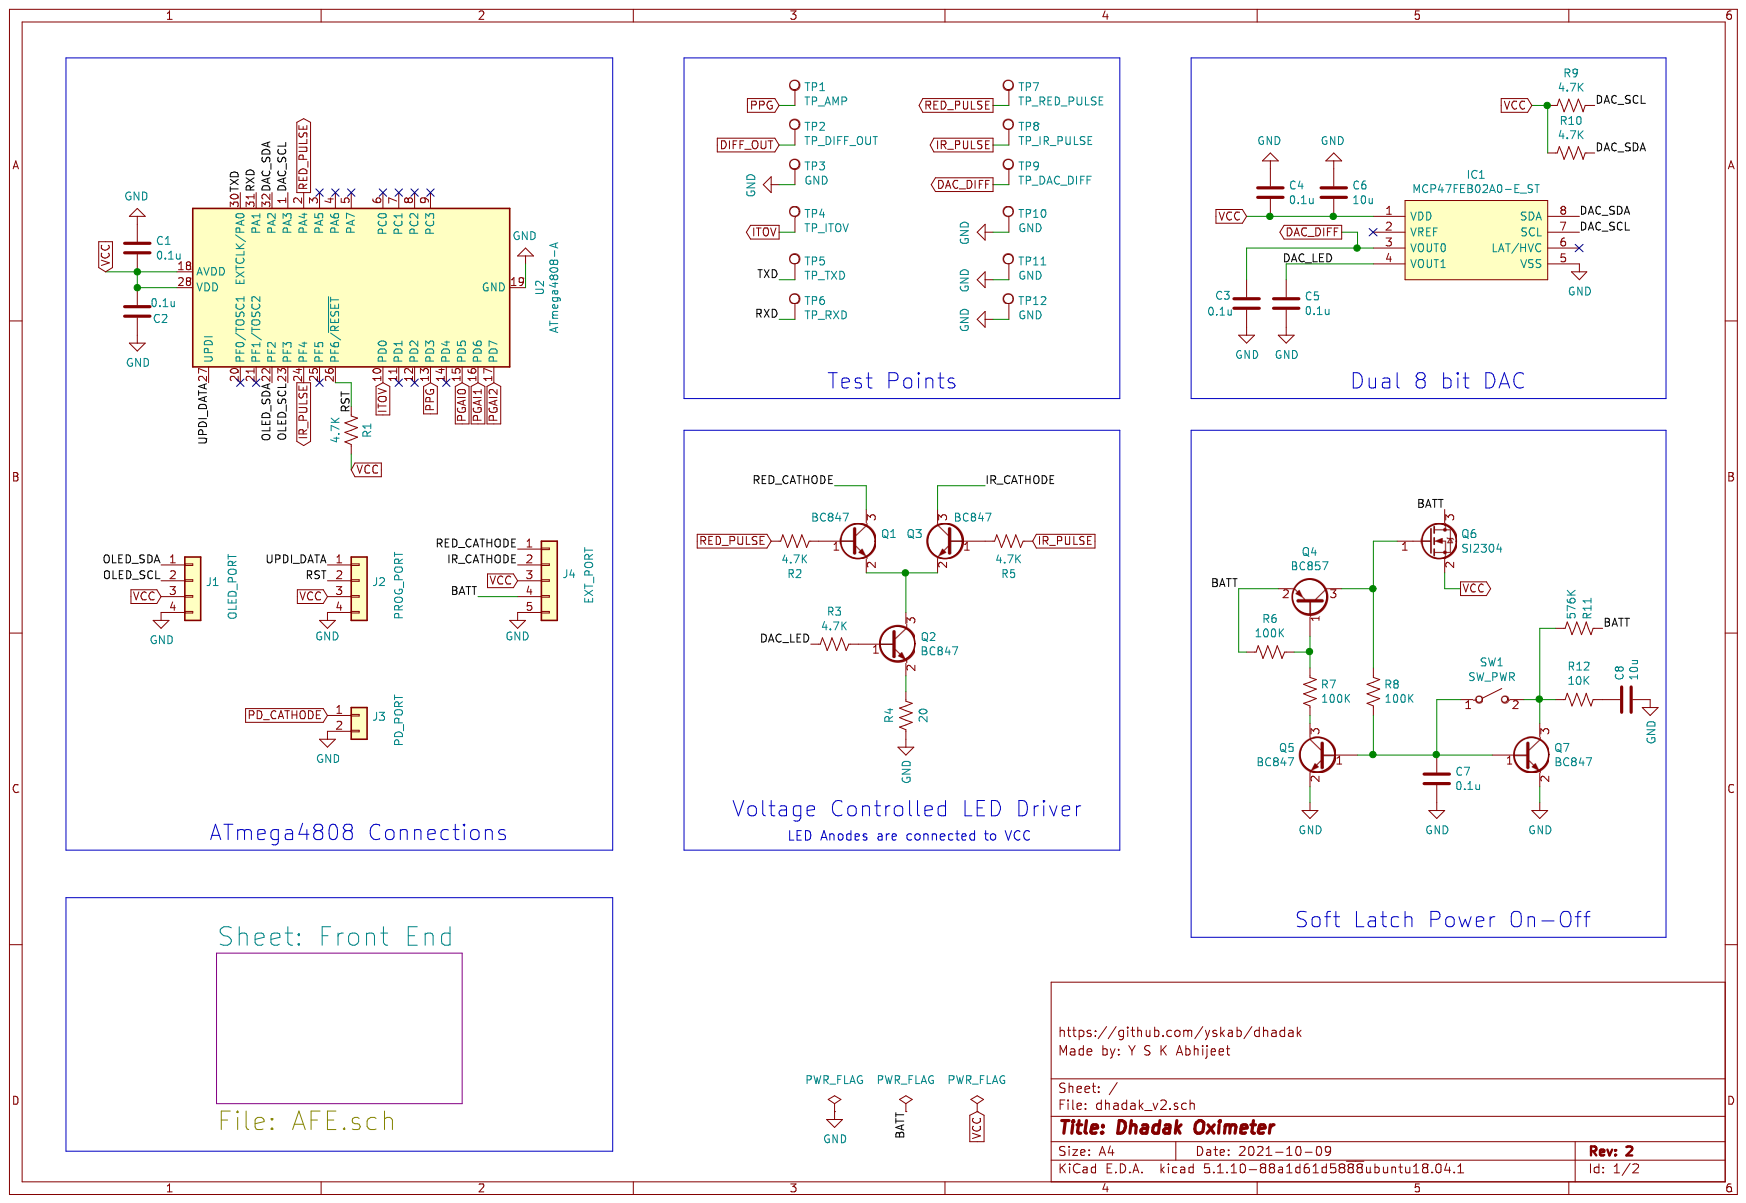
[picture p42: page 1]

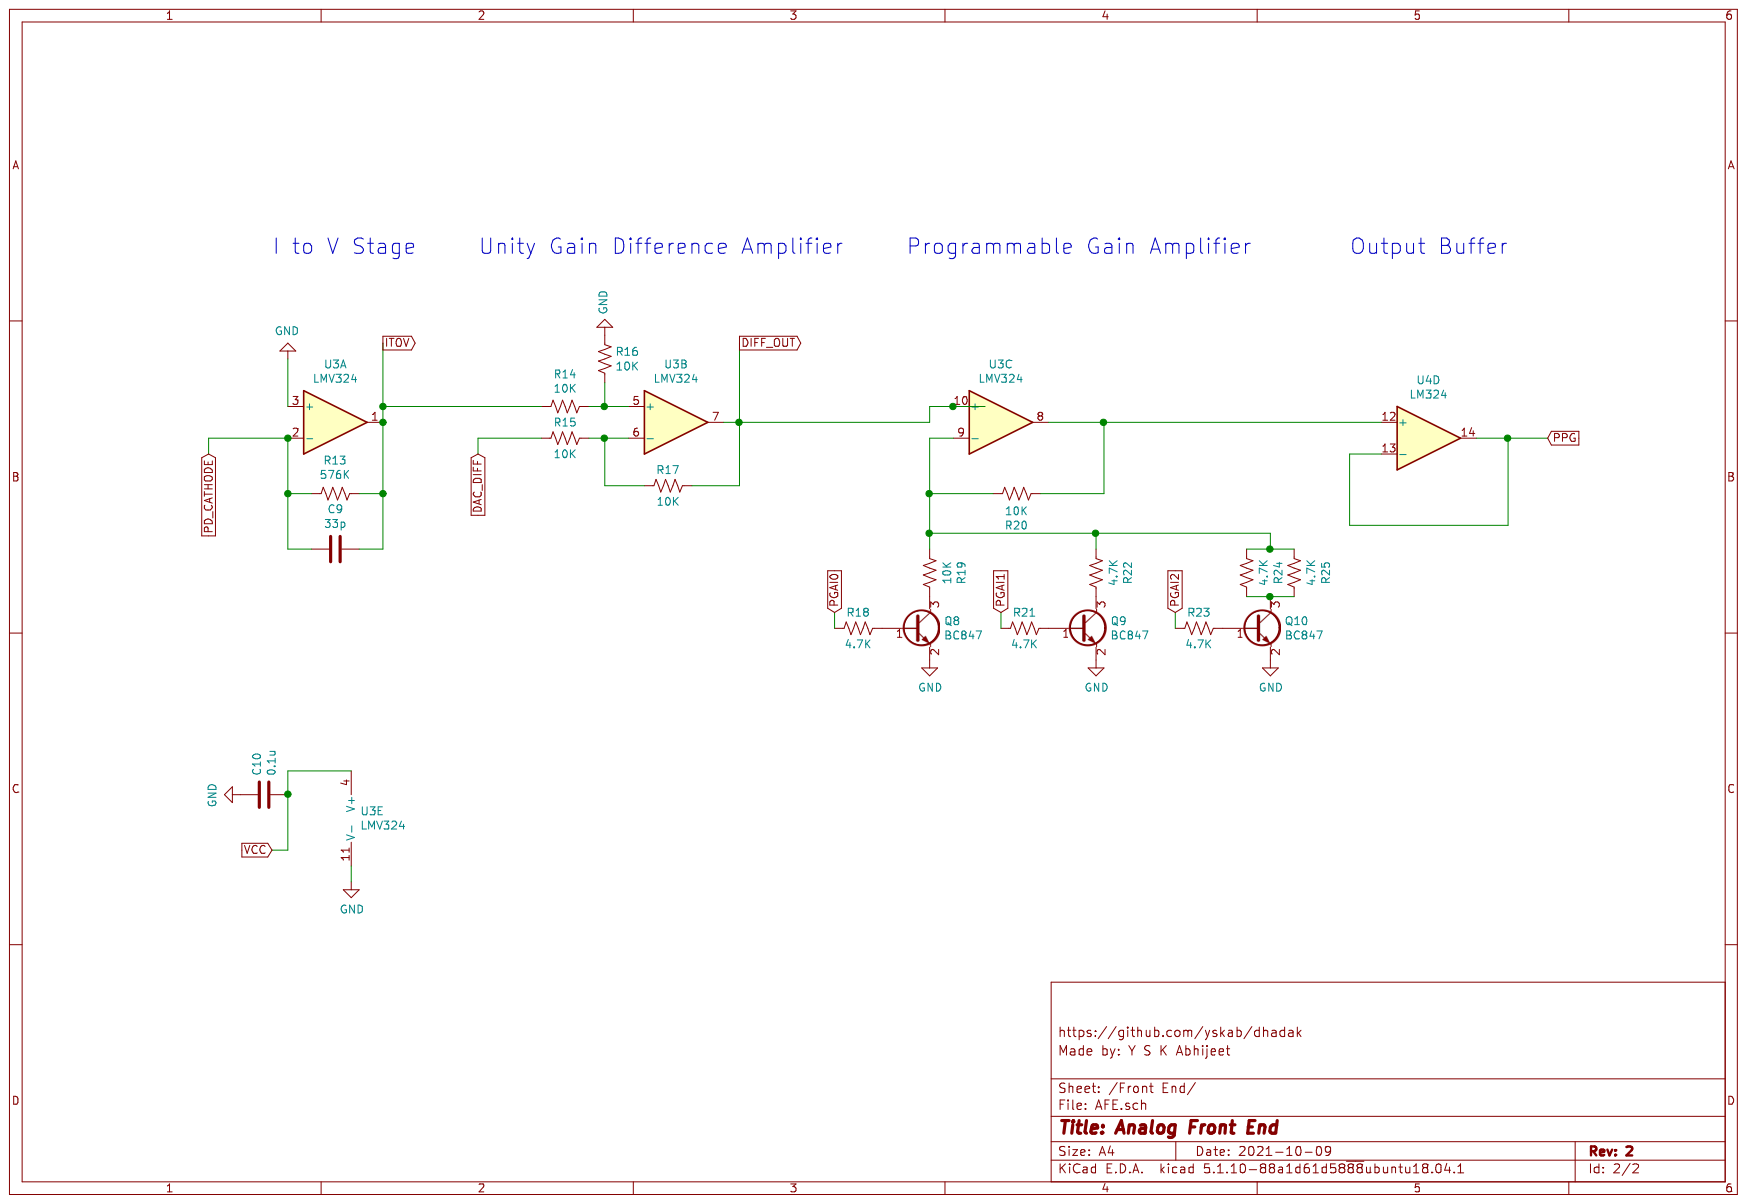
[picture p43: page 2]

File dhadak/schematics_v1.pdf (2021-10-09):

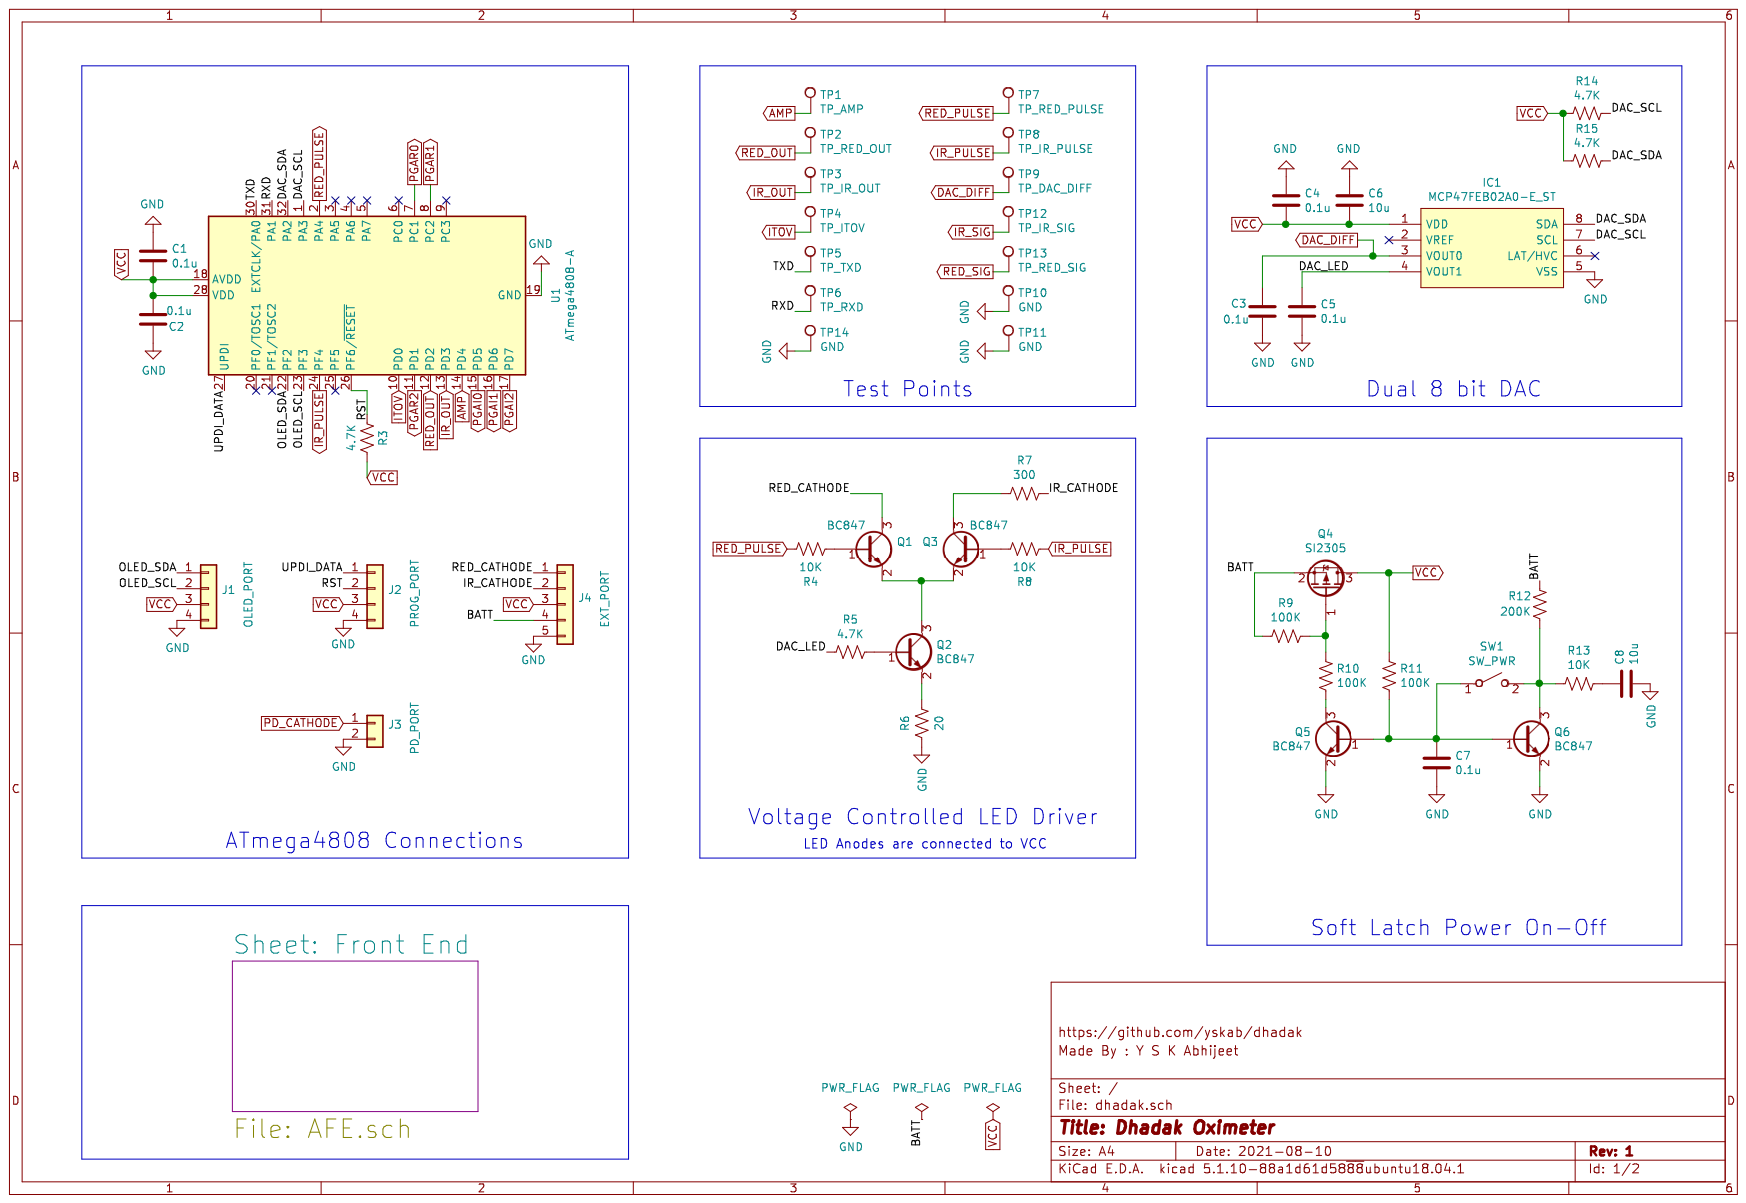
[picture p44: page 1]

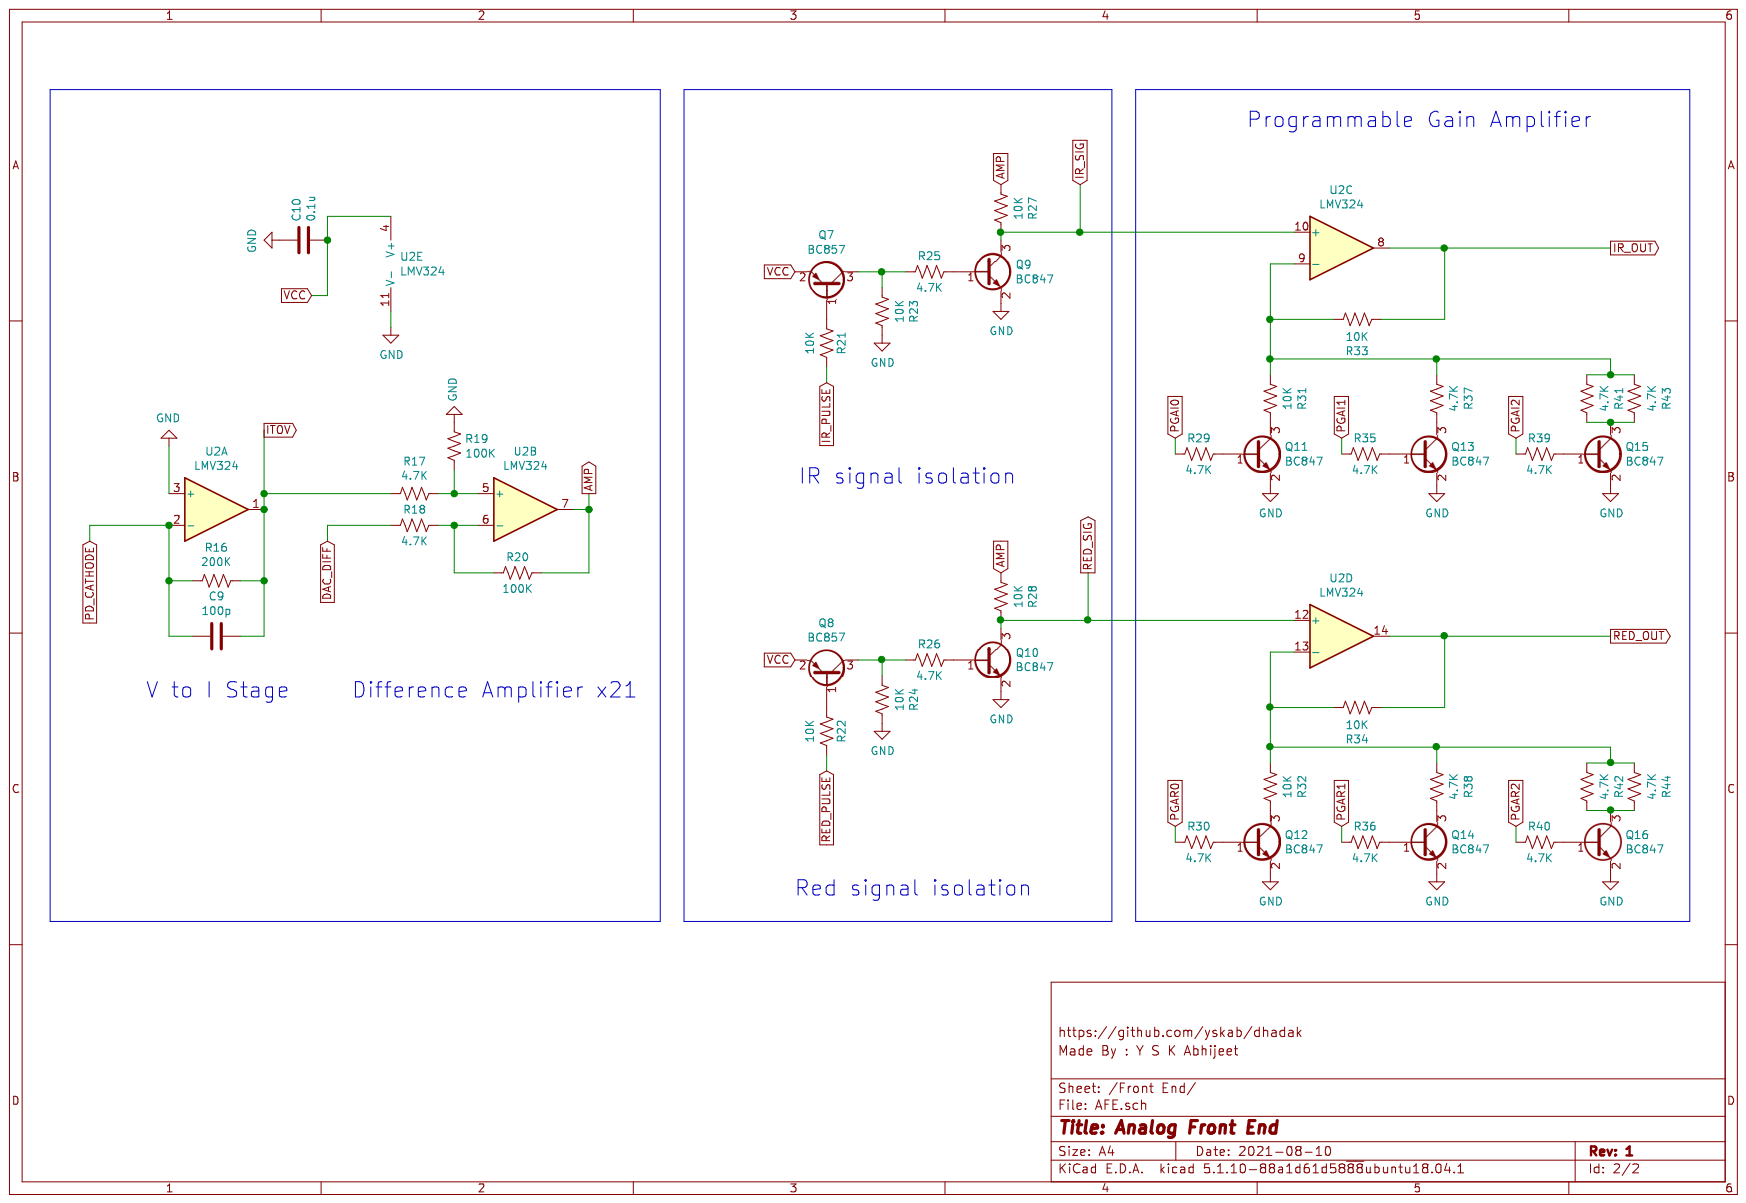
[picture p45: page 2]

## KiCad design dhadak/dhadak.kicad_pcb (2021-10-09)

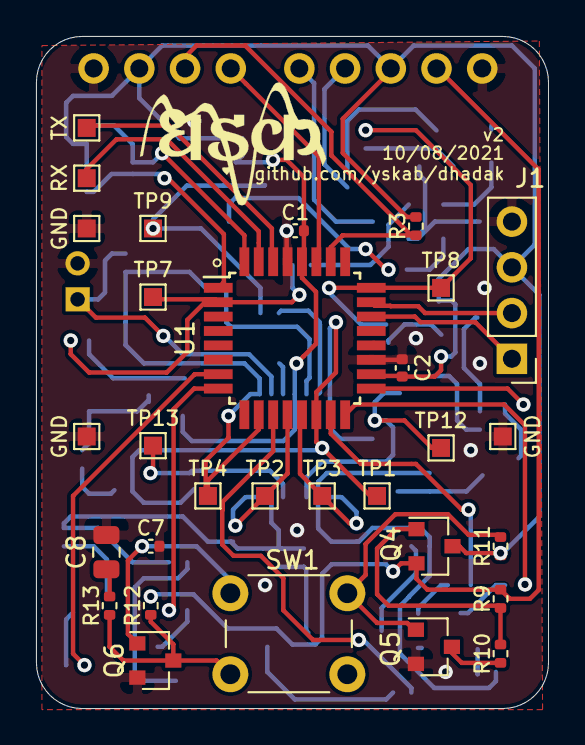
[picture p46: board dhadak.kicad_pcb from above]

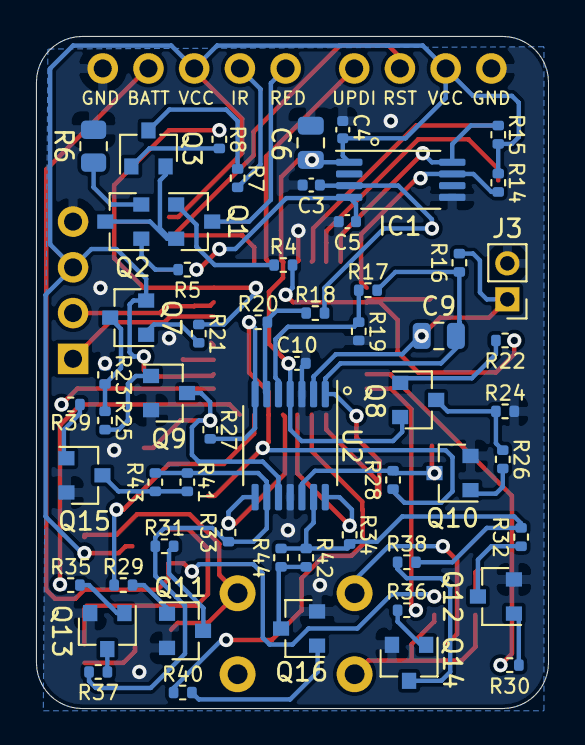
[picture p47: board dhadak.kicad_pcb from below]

Board: 2 copper layers, 28.4 x 37.3 mm, 90 parts (58 on the bottom side), 63 nets.

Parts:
C1, C2, C3, C4, C5, C7, C10: 0.1u; C_0402_1005Metric
C6, C8: 10u; C_0805_2012Metric
C9: 100p; C_0805_2012Metric
IC1: MCP47FEB02A0-E_ST; TSSOP-8_4.4x3mm_P0.65mm
J1: OLED_PORT; PinHeader_1x04_P2.54mm_Vertical
J2: PROG_PORT; PinHeader_1x04_P2.54mm_Vertical
J3: PD_PORT; PinHeader_1x02_P2.00mm_Vertical
J4: EXT_PORT; PinHeader_1x05_P2.54mm_Vertical
Q1, Q2, Q3, Q5, Q6, Q9, Q10, Q11, Q12, Q13, Q14, Q15, Q16: BC847; SOT-23
Q4: SI2305; SOT-23
Q7, Q8: BC857; SOT-23
R3, R5, R14, R15, R17, R18, R25, R26, R29, R30, R35, R36, R37, R38, R39, R40, R41, R42, R43, R44: 4.7K; R_0402_1005Metric
R4, R8, R13, R21, R22, R23, R24, R27, R28, R31, R32, R33, R34: 10K; R_0402_1005Metric
R6: 20; R_0805_2012Metric
R7: 300; R_0402_1005Metric
R9, R10, R11, R19, R20: 100K; R_0402_1005Metric
R12, R16: 200K; R_0402_1005Metric
SW1: SW_PWR; SW_PUSH_6mm
TP1: TP_AMP; TestPoint_Pad_1.0x1.0mm
TP2: TP_RED_OUT; TestPoint_Pad_1.0x1.0mm
TP3: TP_IR_OUT; TestPoint_Pad_1.0x1.0mm
TP4: TP_ITOV; TestPoint_Pad_1.0x1.0mm
TP5: TP_TXD; TestPoint_Pad_1.0x1.0mm
TP6: TP_RXD; TestPoint_Pad_1.0x1.0mm
TP7: TP_RED_PULSE; TestPoint_Pad_1.0x1.0mm
TP8: TP_IR_PULSE; TestPoint_Pad_1.0x1.0mm
TP9: TP_DAC_DIFF; TestPoint_Pad_1.0x1.0mm
TP10, TP11, TP14: GND; TestPoint_Pad_1.0x1.0mm
TP12: TP_IR_SIG; TestPoint_Pad_1.0x1.0mm
TP13: TP_RED_SIG; TestPoint_Pad_1.0x1.0mm
U1: ATmega4808-A; TQFP-32_7x7mm_P0.8mm
U2: LMV324; TSSOP-14_4.4x5mm_P0.65mm

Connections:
/BATT: J4.4, Q4.2, R9.1, R12.2
/DAC_LED: C5.1, IC1.4, R5.2
/DAC_SCL: IC1.7, R14.1, U1.1
/DAC_SDA: IC1.8, R15.1, U1.32
/IR_CATHODE: J4.2, R7.2
/OLED_SCL: J1.2, U1.23
/OLED_SDA: J1.1, U1.22
/RED_CATHODE: J4.1, Q1.3
/RST: J2.2, R3.1, U1.26
/RXD: TP6.1, U1.31
/TXD: TP5.1, U1.30
/UPDI_DATA: J2.1, U1.27
AMP: R20.1, R27.2, R28.2, TP1.1, U1.14, U2.7
DAC_DIFF: C3.1, IC1.3, R18.2, TP9.1
GND: C1.1, C2.1, C3.2, C4.1, C5.2, C6.1, C7.2, C8.2, C10.1, IC1.5, J1.4, J2.4, J3.2, J4.5, Q5.2, Q6.2, Q9.2, Q10.2, Q11.2, Q12.2, Q13.2, Q14.2, Q15.2, Q16.2, R6.1, R19.1, R23.1, R24.1, TP10.1, TP11.1, TP14.1, U1.19, U1.29, U2.3, U2.11
IR_OUT: R33.2, TP3.1, U1.13, U2.8
IR_PULSE: R8.1, R21.1, TP8.1, U1.24
IR_SIG: Q9.3, R27.1, TP12.1, U2.10
ITOV: C9.1, R16.2, R17.2, TP4.1, U1.10, U2.1
unnamed: C7.1, Q5.1, Q6.1, R11.2, SW1.1
unnamed: C8.1, R13.2
unnamed: Q1.1, R4.1
unnamed: Q1.2, Q2.3, Q3.2
unnamed: Q2.1, R5.1
unnamed: Q2.2, R6.2
unnamed: Q3.1, R8.2
unnamed: Q3.3, R7.1
unnamed: Q4.1, R9.2, R10.1
unnamed: Q5.3, R10.2
unnamed: Q6.3, R12.1, R13.1, SW1.2
unnamed: Q7.1, R21.2
unnamed: Q7.3, R23.2, R25.2
unnamed: Q8.1, R22.2
unnamed: Q8.3, R24.2, R26.2
unnamed: Q9.1, R25.1
unnamed: Q10.1, R26.1
unnamed: Q11.1, R29.1
unnamed: Q11.3, R31.1
unnamed: Q12.1, R30.1
unnamed: Q12.3, R32.1
unnamed: Q13.1, R35.1
unnamed: Q13.3, R37.1
unnamed: Q14.1, R36.1
unnamed: Q14.3, R38.1
unnamed: Q15.1, R39.1
unnamed: Q15.3, R41.1, R43.1
unnamed: Q16.1, R40.1
unnamed: Q16.3, R42.1, R44.1
unnamed: R17.1, R19.2, U2.5
unnamed: R18.1, R20.2, U2.6
unnamed: R31.2, R33.1, R37.2, R41.2, R43.2, U2.9
unnamed: R32.2, R34.1, R38.2, R42.2, R44.2, U2.13
PD_CATHODE: C9.2, J3.1, R16.1, U2.2
PGAI0: R29.2, U1.15
PGAI1: R35.2, U1.16
PGAI2: R39.2, U1.17
PGAR0: R30.2, U1.7
PGAR1: R36.2, U1.8
PGAR2: R40.2, U1.11
RED_OUT: R34.2, TP2.1, U1.12, U2.14
RED_PULSE: R4.2, R22.1, TP7.1, U1.2
RED_SIG: Q10.3, R28.1, TP13.1, U2.12
VCC: C1.2, C2.2, C4.2, C6.2, C10.2, IC1.1, J1.3, J2.3, J4.3, Q4.3, Q7.2, Q8.2, R3.2, R11.1, R14.2, R15.2, U1.18, U1.28, U2.4

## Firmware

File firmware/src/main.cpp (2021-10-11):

/*
  Author:    Y S K Abhijeet
  License:   MIT License

  Copyright (c) 2021 Y S K Abhijeet


  This software is licensed under the MIT License(http://opensource.org/licenses/MIT).

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

  This program will calculate the SpO2% and Heart rate of subject.

  ********************Program Flow********************************

  Find red/ir signal levels
  Change intensity until within acceptable levels
  Find required gain level and amplify the signal
  Filter the samples
  Read samples for SpO2 and HR calculation

  ********************Consulted Reference Papers******************

  For Heart Rate:

  ArgÃijello-Prada, Erick Javier. The mountaineer’s method for
  peak detection in photoplethysmographic signals. Revista Facul-
  tad De Ingenieria-universidad De Antioquia 2018 (2019): 42-50
  https://api.semanticscholar.org/CorpusID:116767900

  For SpO2:

  Michael W. Wukitsch, BA,Michael T. Petterson, BA, RRT, CPFT,
  David R. Tobler, BSEE,and Jonas A. Pologe, BSEE
  PULSE OXIMETRY: ANALYSIS OF THEORY,TECHNOLO6Y, AND PRACTICE
  https://link.springer.com/article/10.1007%2FBF01617328


  **********************Used External Libraries********************

  OLED Library
  ssd1306 by lexus2k
  https://github.com/lexus2k/ssd1306

  changed user_settings.h for software I2C mode
  changed ssd1306_i2c_embedded.c for ATmega4808 ports 
  changed ssd1306_i2c_conf.h to add ATmega4808 i2c pins

  To view OLED Images
  bmp2hex by Robert Gallup
  https://github.com/robertgallup/python-bmp2hex
  Process:
  - get your image
  - invert, resize as per display(128x64) and change to 1-bit mode on GIMP
  - export image as bmp
  - run: python3 bmp2hex.py -w 8 -x -i image.bmp  > out.c
  - copy the array in out.c to bitmap.h 

  ***********************Programming Info**************************

  One Time Activity - change device fuse for 8Mhz internal oscillitor.
  https://docs.platformio.org/en/latest/platforms/atmelmegaavr.html
  I was not able to get that done via PIO, so i used jtag2updi package
  https://github.com/ElTangas/jtag2updi and https://github.com/MCUdude/MegaCoreX
  selected Clock: Internal 8 MHz, uploaded to device via Arduino IDE.

  Programming Device - 
  used CP2102 usb to serial adapter for programming with UPDI interface
  via pyupdi https://github.com/mraardvark/pyupdi

  Upload and platform options in platformio.ini file.
  Any docs mentioned here in comments are present in project's reference folder
*/

#include <Arduino.h>
#include <Wire.h>
#include "../lib/ssd1306/src/ssd1306.h"
#include "bitmaps.h"


#define IR_PULSE_PIN PIN_PF4    //IR Pulse signal Pin
#define RED_PULSE_PIN PIN_PA4   //RED Pulse signal Pin
#define ITOV_PIN PIN_PD0        //ITOV stage output Pin
#define PPG_PIN PIN_PD3         //Signal Output Pin

//8bit DAC - MCP47FEB02A0
#define DAC_SDA_PIN PIN_PA2
#define DAC_SCL_PIN PIN_PA3
#define DAC_ADDR 0x60           //DAC I2c device Address
#define DAC_LED_REG 0x08        //DAC output register address mapped to VOUT1
#define DAC_DIFF_REG 0x00       //DAC output register address mapped to VOUT0

//OLED Pins
#define OLED_SDA 2
#define OLED_SCL 3
#define OLED_ADDR 0x3C

#define SAMP_N 20               //Number of SpO2 samples to weight for calculation

//PGA Pins
enum PGAI {
  PGAI0 = 17,
  PGAI1,
  PGAI2
};

uint8_t state;
unsigned long now;


uint16_t red_itov,
         ir_itov,
         ir_itov_max,
         ir_itov_min,
         red_itov_min,
         red_itov_max,
         ambient;

uint16_t ir_amp,
         ir_amp_prev = 0,
         red_amp,
         red_amp_prev = 0;

uint8_t dac_ir_level = 0,
        dac_red_level = 0,
        dac_low_level = 40;

uint16_t ir_out,
         red_out,
         red_out_prev = 0,
         ir_out_prev = 0;

bool is_red_peak = 0,
     is_ir_peak = 0,
     ir_led_set = 0,
     red_led_set = 0,
     start_disp = 0;

uint8_t red_ctr = 0,
        ir_ctr = 0,
        red_comp = 30,
        ir_comp = 30;

uint8_t ir_hr,
        red_hr,
        hr = 0;

unsigned long ir_t_prev = 0,
              red_t_prev = 0,
              red_t,
              ir_t;

uint8_t led_level_red = 60;
uint8_t led_level_ir = 60;

//Butterworth 1st order coefficients for 500hz sampling rate
float a2 = -0.95937;
float b = 0.020316;

//Parameters for SpO2 calculation
uint16_t spo2_wt[SAMP_N] = {0};         //Array of Weighted samples
uint8_t wt[SAMP_N] = {0};               //Array of Weights
uint8_t spo2_avg = 99;                  //Inital average SpO2
uint8_t sample_n = 0;                   //Samples Counter
uint8_t spo2_avg_in[SAMP_N/2] = {0};    //Array of Weighted Averages
uint8_t spo2_ctr = 0;                   //Average Samples Counter

/*
Reference Doc - AN2447: Measure VCC/Battery Voltage Without Using I/O Pin
http://ww1.microchip.com/downloads/en/AppNotes/00002447A.pdf
*/
uint8_t calc_battery_level()
{
  //set VREF of AC0 to internal voltage 2.5V
  VREF.CTRLA = 0x02;

  //set required DACREF voltage, setting VDACREF to 2.5V
  //for 2 AAA batteries, 2.5V would be considered as dead - 0% 
  AC0.DACREF = 0xFF;

  //set ADC ref to VCC for comparison, DIV256 prescalar setting
  //result dosent populate correctly for lower division factors
  ADC0.CTRLC = 87;

  //now set ADC mux for DACREF input
  ADC0.MUXPOS = 0x1C;

  //start ADC,10bit resolution, in single mode
  ADC0.CTRLA = 0x1;  
 
  //start conversion
  ADC0.COMMAND = 0x01;
  /* Wait for result ready */
  while (!(ADC0.INTFLAGS & ADC_RESRDY_bm));

  uint16_t res = ADC0.RES;

  /*
  Assuming a healthy battery to have voltage 3.1V, RES would be
  (1023/3.1)*2.5 = 825, anything below this value considered as full(99%)
  if res is 1023, ADC ref = DACREF, consider battery as dead(0%)
  in between, calculate percentages linearly
  in practise, change battery if below 50% as oled might not turn on properly for
  voltages below 2.8V

  I used duracell AAA batteries, MN2400
  https://www.duracell.com/wp-content/uploads/2020/02/MN24US1119.pdf
  lets consider 2.7 as threshold and max average device current draw is 25mA
  from datasheet, continuous operation period should be around 13hrs.
  */

  uint8_t battery_perc;

  if(res <= 825)
    battery_perc = 99;
  else
    battery_perc = (1023 - res)/2;

  return battery_perc;

}

//Sets the required Ouput register of DAC
void set_DAC(uint8_t reg, uint8_t val)
{

  Wire.beginTransmission(DAC_ADDR);
	Wire.write(reg);
  Wire.write(0);                      //1st word byte always zero for 8bit DAC as in datasheet
  Wire.write(val); 
  Wire.endTransmission(); 

}

void set_DAC_diff(uint8_t level)
{
  set_DAC(DAC_DIFF_REG, level);
  delayMicroseconds(10); //Small delay to avoid ringing on edge to be considered in difference Amp Stage            
}


uint16_t low_pass_filter(uint16_t x, uint16_t x_prev, uint16_t filt_out_prev)
{
    //1st order IIR low pass filter.    
    uint16_t filt_out = b*x + b*x_prev - a2*filt_out_prev;
    return filt_out;
}


void setup()
{
  Serial.begin(230400);          

  //calc battery percentage
  uint8_t batp = calc_battery_level();
  char batp_str[4];
  sprintf(batp_str, "%d%%", batp);   

  //Initialize OLED Display, SCL/SDA Pins as per PORTF(PF2/PF3)
  ssd1306_128x64_i2c_initEx(OLED_SCL,OLED_SDA,OLED_ADDR);
  ssd1306_clearScreen();
  /*Was not able to use BMP images with Bitmap function,images were not showing properly
  hence used bmp2hex to convert to xbmp and used XBitmap function,images appear fine now.*/

  //Logos displayed in wait state, until parameters are found
  ssd1306_drawXBitmap(0, 0, 87, 64, dhadak_logo);
  ssd1306_drawXBitmap(95, 2, 24, 24, battery_logo);
  ssd1306_setFixedFont(courier_new_font11x16_digits);
  ssd1306_printFixed(95,0,batp_str, STYLE_NORMAL);
  ssd1306_setFixedFont(ssd1306xled_font6x8);
  ssd1306_printFixed(0,56, "Please wait 15secs...", STYLE_NORMAL);
  ssd1306_setFixedFont(comic_sans_font24x32_123);

  pinMode(IR_PULSE_PIN,OUTPUT);
  pinMode(RED_PULSE_PIN,OUTPUT);

  //initially no PGA engaged
  pinMode(PGAI0,OUTPUT);
  pinMode(PGAI1,OUTPUT);
  pinMode(PGAI2,OUTPUT);
  digitalWrite(PGAI0,LOW);
  digitalWrite(PGAI1,LOW);
  digitalWrite(PGAI2,LOW);


  //initialize I2C for DAC communication
  Wire.begin();                           //default Pins 32 - SDA, 1 - SCL for I2C 
  Wire.setClock(400000);

  //Set LED DAC to off initially
  set_DAC(DAC_LED_REG,0);    
            
  //set internal VREF to 1.1
  VREF.CTRLA = 0x10;
  
  state = 0;
  Serial.println("Initialization Complete");
}
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

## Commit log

2021-10-09 Added Kicad Project for v1
    [AFE.sch, BOM.ods, dhadak-B_Cu.gbl, dhadak-B_Mask.gbs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]
2021-10-09 Changed title of 2nd decision box in flow chart
2021-10-09 Added Enclosure files
    [3mm_LED.stp, AAA Batterie.step, Fairchild_-_QSB34CGR.step, bot_base.stl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]
2021-10-09 Added v2 Kicad project
    [AFE.sch, dhadak.sch, dhadak_v2.kicad_pcb, dhadak_v2.sch]
2021-10-10 Added battery consumption comment
